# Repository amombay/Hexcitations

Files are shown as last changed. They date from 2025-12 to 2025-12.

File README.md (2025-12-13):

# Hexcitations
ENGN1735: Vibrations of Mechanical Systems Design Project, Active Particles
<div align="center">
  
</div>

Hexcitations is a design project for Brown University's School of Engineering course, ENGN1735: Vibrations of Mechanical Systems, completed by Andrew Mombay, Kaya Bruno, Helen Primis, and Sarah Nguyen in collaboration with the Harris Lab inclusive of Jack-William Barotta and Daniel Harris.

## Organization of this Repository
This repository contains the following folders:
- CAD Designs: This serves as the general purpose folder containing all CAD designs completed throughout the project, represented across the different iterations and phases of the project.
  - Cage Design: This sub-folder contains all designs of our cages, beginning with our circular cage model before moving to the rectangular, back-held cage model.
    - Iteration I: This sub-folder contains all designs of our intial, circular filament with PVC tubing linkages. These designs were later scrapped and replaced in favor of smaller, more compact linkages as significant issues were faced with friction and mass-dragging due to the sheer weight of the cage and the inability of the hexbug to provide adequate locomotion and movement of the cage for image tracking purposes.
    - Iteration II: This sub-folder contains all designs of our next model where we shifted towards building cages contained on the hexbugs back with a T-shaped marker for tracking purposes along with circular extrusions for the silicone linkages to attach to. This design was later modified and is thus currently redundnant to allow for a better fit on top of the hexbug and silicone linkage.
    - Iteration III: This represents the pre-cursor to our final linkage iteration. Modifications were made to the cage to encourage a better fit of both the cage and silicone linkage.
    - Iteration IV (Final): This represents our most current linkage with spacing for the QR codes for tracking and ensures best-fit for the hexbugs.
  - Linkage Design: This sub-folder contains all linkage mold designs including the 3.5, 4.5, and 5.5mm linkage molds.
    - Iteration I: This sub-folder contains all initial linkage mold designs
    - Iteration II (Final): This sub-folder contains all final linkage mold designs, including the 'key' mold design applied in our final experiemental model.
    - Iteration III (In progress): This sub-folder contains experimental mold designs that should not be used until further work is completed to prevent silicone leakage out of the mold. These molds are currently being explored to reduce extra silicone pieces around the mold and to enhance curing conditons.
  - Misc: This sub-filder contains all additional designs related to constraining the hexbugs movement such as a pole mount, jellyfish-modeled head, and final hexbug stations.
 - MATLAB: This serves as the general purpose folder containing all code regarding finding the material properties and constants along with all code needed to mock simulations of behaviors.
   - Iteration I: This sub-folder contained all previous versions of source code, inclusive of estimating material parameters, generating movies of simualtions, simulating behavior, and our initial tracking software. This code is currently redundant and encapsulated in our second iteration of code.
   - Iteration II (final): This sub-folder contains all finalized versions of iteration I, focusing on mocking the actual experiment through simulations and estimating the material properties and constants of the silicone linkages. All code referenced within these two categories is stored in this folder.
 - Tracking: This folder contains python files to track the hexbug filament. This is our final tracking software, utilizing the QR code method to process our videos.
- Written Remarks: This folder contains all written statements produced by the group, inclusive of our presentations, written materials produced (literature reviews, final written report, and more), our bill of materials, sustainability poster, and materials flow sheet.

## Background, Goals, & Modeling Approach
Background: Our project aims to study active particles and observe the collective behaviors and aggregated movement emergent upon coupling through a hexbug-based computational and physical model. In-depth research in this field occurred due to the development of high definition photography which allowed for the detailed scaling of the limb movements for invertebrates and vertebrates. The locomotive functions of the animal's appendages were linked to a central pattern generator in each organism, demonstrating that active particle are driven by autonomous collective movements without the direct influence of a central force. We look to create an accurate model for an adjustable linked filament to mimic cilia-like behaviors by utilizing Hexbugs and 3D-printed Hexbug-like particles to serve as a macroscopic version of the often microscopic particles referenced in the relevant literature. 

Key Goals
- Create an accurate model for an adjustable linked filament to mimic cilia-like behaviors by utilizing Hexbugs, exploring the interplay between the filament elasticity and activity
- Observe and analyze the collective synchronization behavior emergent upon coupling Hexbug active particles with variable bendability
- Investigate four-legged gaits, representative of quadriflagellates by attaching multiple Hexbug filaments to a center pin

Along with each phase of the project, we aim to implement the following modeling approach:
- Physical Modeling: To create the filaments, we plan on using linkages cast from a silicone mold to join the Hexbugs. This allows for semi-constrained movement along the x and y axes. A 3D-printed cage placed on top of each Hexbug allows the linkage to be affixed via prongs, as well as a show a QR code tracking marker to be utilized in Python image processing.
- Mathematical Modeling: Varying lengths of all of the silicone linkages cause the filaments as a whole to have different propensities to bend. To calculate the bendability of the filaments (elastoactive parameter), we first calculate the spring constants to verify the Young’s Modulus. We do this using image processing in MATLAB and can then calculate the corresponding torsional stiffness values and elastoactive parameter. 
- Data Collection: For each phase of this experiment, we use Python ArUco tracking to track the relative position and angular displacement of each Hexbug when fixed at a center point. Using these two elements, we can calculate the mean curvature and polarization for varying configurations of the apparatus upon changing the shape and length of the connection beam, the length of the filament, and the number of hexbugs on each filament.

## Findings & Future Directions
As of now, we have found the following:
- Hexbug filaments serve as an effective means of modeling and experimentally evaluating elasto-active systems in active matter, dynamic systems. Through our variation of both the linkage and filament length, we were able to establish that the onset of oscillation is both a function of the number of Hexbugs in the filament, N, and the σ, the elasto-activity of the linkage, as predicted by our mathematical model. Filaments with smaller values of σ showed straight-line trajectories with the onset of oscillation taking place somewhere between σ = 1.0071 and 1.8800, with higher values of σ producing longer periods of oscillatory behavior. Comparison between the experimental trajectories and the mathematical model showed relative agreement in the oscillation, mode shape, and phase behavior. Whilst quantitative differences remained between both the model and the experimental observations, likely due to friction and active force contributions, the model successfully captured the physics governing filament behaviors.
- Synchronization is possible with elasto-active elements through the application of silicone linkages between Hexbugs. Beyond our findings with single-filament behavior, we saw that Hexbug systems can show both synchronization and phase-locking behaviors. With the two and four-filament systems, we observed both synchronous behaviors in and out-of-phase in addition to desynchronization events likely due to asymmetric linkages, small differences in cage placement, and variations in Hexbug natural frequency. As such, this indicates that our model may allow for close comparison with biological cilia and flagella systems, mimicking complex biological behaviors. In addition, the ability to induce swimming-like modes and rotational motion highlights the ability of our model to study gait and locomotion in active matter systems.

Currently, our model is complete and ready to explore further scientific modeling and synchronization phenomenon. That being said, additional functionality is entirely possible and is highly recommended to reduce error and enhance both the scope and applications of our model. This includes:
- Building individual hexbugs to reduce any ‘drift’ error where the hexbugs have a general tendency to lean towards the right. Such drift is randomized, with some bugs seeing more significant drift than others due to manufacturing differences. As such, building our own hexbugs would eliminate this drift.
- To control for power differences, we could link our individually built hexbugs to a central power supply and eliminate any differences in supplied power to each component.
- To reduce issues in the silicone linkages, further work could be done on the encapsulated molds to prevent leakage and ensure the mold is completely full to reduce the error of excess silicone attached to the link. In addition, controlling the curing conditions with time, humidity, and temperature would enhance the accuracy of our results by unifying the material properties across all links.

Additionally, we pose the following questions as we continue our work:
- Coding/ Simulation Perspective
    - How can we more robustly track the orientation and positioning of our hexbugs beyond QR code tracking? Is there a way to further minimize any sort of “skipping” when some bugs are enduring lots of rotation in a short amount of time?
    - How can we reduce and/or better account for noise in our modeling?
    - Is there a way for us to test the active force of our particular Hexbugs (commercially or in-house) and would this help our simulation mirror what we are seeing in real-life? 
- Hardware and Design Perspective
  - How can we create a DV-powered homemade model to better simulate collective behavior and brownian motion as opposed to our current model?
  - How can we best implement our design to reduce Hexbug drift and skew towards one direction?
  - How can we best optimize and control cure conditions for the silicone linkages and how might other elastomer linkages impact our model? How do linkage length, stiffness, and cage geometry impact the range and modes of motion in our filament system?
  - How can we elicit multi-filament synchronization in Hexbug behavior? Is this theoretically plausible/ possible? To what extent can we see phase-locking and symmetrical movement compared to biological cilia?

 Given all of our remaining questions and findings, we propose the following next steps:
- Revise our physical model
  - By developing our own DV-powered hexbug design, we’d get to see its motion unimpacted by commercial manufacturing and thus get to validate our model without taking into account defects in supplier processing. In addition, this would allow us to control the native skew present in commercially available hexbugs by modifying our own design to reduce any drift effects. In addition, by further controlling the silicone mold curing conditions, we’d be able to enhance the accuracy of our model and ensure reproducibility.
- Improve our tracking software
  - Currently, our tracking software can only handle calculating the mean polarization and the mean curvature of a one-filament system. Expanding on our project, ideally, we would want to be able to accurately track a multifilament system, correctly identifying and tracking what Hexbugs correlate to what filament and comparing their relative angular motion, mean polarization, and mean curvature.
- Explore synchrony conditions
  - Through improving both the tracking and physical model, we would be able to begin enhancing our investigation into synchronization of our multi-filament model of which our findings would prove to be extremely beneficial to the scientific community in exploring how to model active particles to simulate real-world phenomenon.

## Building and Operating Instructions
  In order to build our device, the following steps should be taken:
- Hexbugs:
  - No direct modifications were made to the hexbugs themselves, however, prior to final modeling one should replace all batteries (LR44 coin batteries) in the hexbugs to ensure that power supplied is constant across all bugs.
- 3D Printed Hexbug Cages:
  - All hexbug cages were 3D printed using PLA filament and a BambuLabs A1 printed with an infill of 15%. Following printing, all supports were carefully removed and cages were visually inspected to ensure no damage had occurred.
- Silicone Linkages:
  - Molds were first 3D printed using PLA filament and a BambuLabs A1 printer with an infill of 15%. Four different molds were constructed of various lengths to measure the differences beam length had on bending motion of the filament. Following printing, all molds were visually inspected and supports were carefully removed to reduce the risk of breaking the mold. Our first renditions of the silicone molds were non-encapsulated whereas our final molds employed used a 2-piece, encapsulated system with pins used to ensure proper fit and mold orientation when casting.
  - To create the silicone mixture, we used a 2-part mixture and utilized a scale to carefully measure out 20 grams part A and 20 grams part B of the mixture to ensure equal aliquots were used. This was then thoroughly mixed using a wooden popsicle stick and then poured carefully into the molds. Molds were purposefully overfilled to ensure all parts of the mold were uniformly filled. Molds were then cured in open-air conditions at 70F and humidities of 20-50% for at least 24 hours.
  - Following a cure time of at least 24 hours, the linkages were then carefully pulled from their molds, visually inspected for any deformities, and excess silicone was trimmed off.
- Central Body/ Hexbug ‘Station’:
  - All versions of the hexbug station, circular, rectangular, and individual were 3D printed using PLA filament and a BambuLabs A1 printer with an infill of 15%. Following printing, all supports were carefully removed and the station was visually inspected to ensure no damage had occurred.
- Hexbug Station and Hexbug Cage Silicone Clips:
  - Both versions of the Hexbug silicone clips for the station and cages were 3D printed using PLA filament and a BambuLabs A1 printer with an infill of 15%. Following printing, all supports were carefully removed and the clips were visually inspected to ensure no damage had occurred.
- QR Codes:
  - All QR codes were printed on standard 8x11 A4 paper and carefully cut out to ensure the QR code had a white border to ensure accurate tracking due to the color of the Hexbug cage filament (black). 

Upon finishing all individual components, the cages were placed on top of the Hexbug and adjusted until the fit was snug and the Hexbug was pushed as far forward as possible against the cage’s front ‘fence’ to ensure uniform fit across all hexbugs. The linkages were then placed into the pin and the PLA silicone clips were clamped down onto the linkage until snug. The frontmost cage was then connected to the station and the station silicone clip was used to secure the Hexbug filament to the station. Finally, double sided tape was used to secure the QR codes onto the back of each bug for tracking purposes.

In order to operate our device, the following steps should be taken:
- After the finalized assembly is complete, as described above, the full assembly was placed on a white backing sheet for contrast and a tripod was set up to record the filament’s oscillations.
- Each bug was then individually turned on and the filament was then recorded. After recording was complete, videos were saved and all post-processing of the video was then conducted in Python and compared to the simulation predictions done in MATLAB.

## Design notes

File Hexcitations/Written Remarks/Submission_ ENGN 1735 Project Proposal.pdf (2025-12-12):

ENGN1735 Active Particles Project Proposal Sarah Nguyen, Helen Primis, Andrew Mombay, & Kaya Bruno Mentor: Jack-William Barotta
Due October 14, 2025
Project Name: HexCitations

Contents:

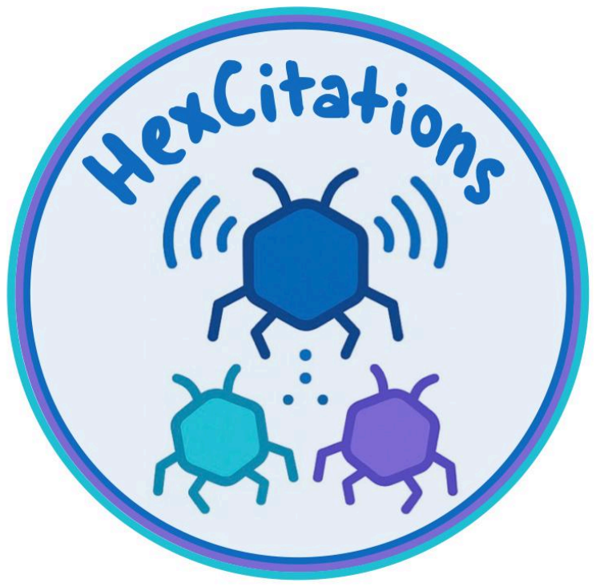
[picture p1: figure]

### 1. Background and Brief Literature Review 2. Key Questions 3. Experimental Workflow and Schematics

a. Phase I
b. Phase II
c. Phase III

### 4. Data Collection and Aim of Iteration

a. Phase I
b. Phase II
c. Phase III

### 5. Modeling, Numerical Techniques, and Materials 6. Semester Timeline and Group Member Roles 7. Project Deliverables and Transfer of Knowledge 8. Appendix

a. Bibliography

### 1. Background and Brief Literature Review

The background of our project lies with the study of active particles and observations of the collective behaviors emergent upon coupling. Unlike true Brownian motion, linked active particles harness their own energy and have the capability for complex collective behaviors to arise.

1 There is
evidence of collective behaviors with active particles resulting in self-propelling locomotive functions, resource collection, local environmental restructuring, and particle aggregation.

2 The foundations of this
study are cited as being rooted back to the philosophical fundamentals of Aristotle: the whole is greater than the sum of parts.

3 Considering the example of biotechnically-based robotics systems, the behavior of active particles is driven by autonomous collective movements without the direct influence of some sort of central force; the critical nature of this study is how the “random” particles, when linked together, result in an aggregated movement.
The onset of research in this field occurred due to the development of high definition photography which allowed for the detailed scaling of the limb movements for invertebrates and vertebrates. The locomotive functions of the animal's appendages were linked to a central pattern generator in each organism that did not send feedback to the neural system thereby enacting the movement. This is connected to our investigation of aggregated movement mentioned in the previous paragraph.

4 Different
locomotive actions can be linked to a certain number of filaments stemming from a fixated central body. Two appendages could represent swimming, four could represent trotting, eight could represent rotary breast stroke of flagella, and sixteen could mimic the wave motion of a series of cilia.

5 The study of
collective behaviors usually falls under the Viscek model which focuses on the emergence of scaled dynamics from independent particles. The model exists with much freedom, saying “The only rule of the model is that at each time step a given particle driven with a constant absolute velocity assumes the average direction of motion of the particles in its neighborhood with some random perturbation added.”

6
Sources cite the alignment of velocities as a result of both self-propelled forces and “social forces,” when applicable.

7
Taking the somewhat disconnected but overarching plethora of research in the realm of active particle behavior, our project aims to employ Hexbugs and 3D-printed Hexbug-like particles to serve as a macroscopic version of the often microscopic particles referenced in the relevant literature.

8
Understanding and taking into account that the inertia of our active particles can affect the linked movements of our systems, we will aim to create an accurate model for an adjustable linked filament to mimic cilia-like behaviors. The first rendition of this filament will be battery based, with a second stage evolution resulting in a direct voltage sourced filament which is independent of batteries in the active particles. Time permitting, we will apply our filament model to model the appendage based movement of a jellyfish and explore how different orientations and combinations of filament power and length affect the velocity of our model’s movement.

9 Our key questions and project workflow are outlined below in this project proposal.

9 Miles, Jason G, et al., 3.

8 3D Printable Hexbug Design and Instructions, Blog Link. (https://stldenise3d.com/vibrobugs-3d-printed-brush-bots/)

7
Ibid, 4.

6 Baconnier, et al, 3.

5
Ibid, 3.

4 Wan, 2.

3 Levay, et al., 2.

2 Sinaasappel, et al., 1.

1 Barona Balda, et al., 847.

### 2. Key Questions

A. How can we build a cilia-like filament by employing 3D-printable hexbugs and mechatronic principles?
B. How do different orientations of hexbug coupling influence their collective actuation?
C. How does spring stiffness influence synchronization and sustained oscillations in elastic networks?
D. Can we achieve biomimicry with our model?

### 3. Experimental Workflow and Schematics

a. Phase I:
For the first experimental phase of this project, we will utilize Hexbug Nanos from the Harris lab as the macroscopic active particles within the filament. We will design shells to contain each particle and provide a linkage point between each discrete bug. The filament will be attached to one fixed non-powered source, such as a cilia attached to the parent body.
b. Phase II

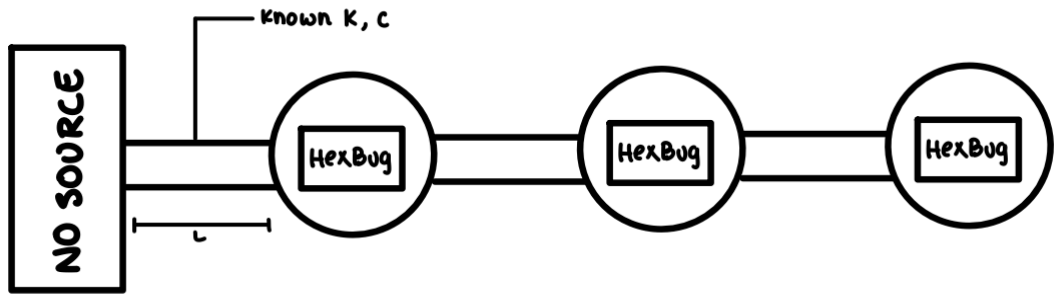
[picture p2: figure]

For the second phase, we will 3D print and construct Hexbugs that can be connected via wiring to a fixed direct voltage source, eliminating the need of the battery powered Hexbug Nanos. This design will be modular to allow for adjustable filament length and attachments.

c. Phase III

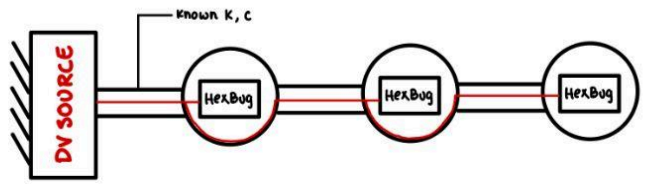
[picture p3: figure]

Time permitting, we will engage with the concept of biomimicry using the DV-source based filament design by having multiple appendages attached to one unfixed central body, mimicking a jellyfish. The goal of this phase is to investigate the Hexbug orientations that move the fastest, considering different lengths and numbers of cilia attached to the beam.

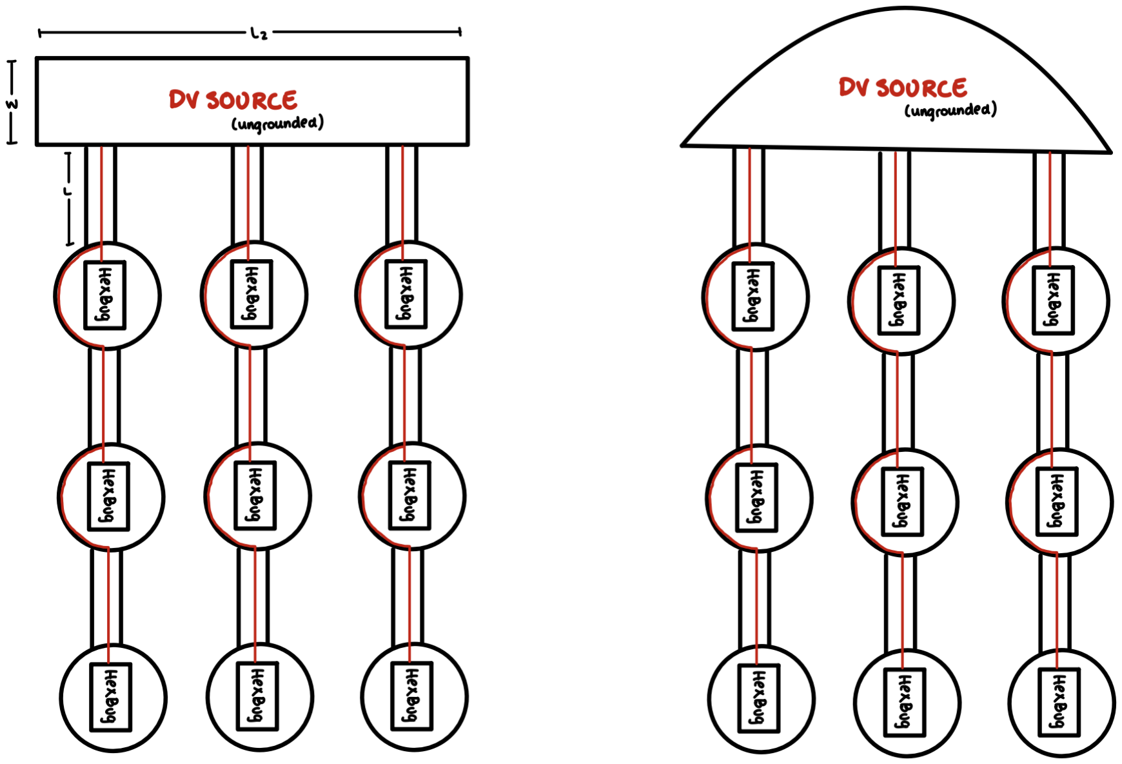
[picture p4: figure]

### 4. Data Collection and Purpose of Iteration

a. Phase I: For the first iteration of our filament, we will use MATLAB image tracking to track the relative displacements and velocities of each particle to the fixed base. The purpose of this iteration is to understand the aggregate movement of the linked active particles when using battery-based Hexbugs and get a strong foundational prototype for future facets.
b. Phase II: For the second phase, we will perform the same data collection set as Phase 1, now employing a DV source based model instead of the battery Hexbugs to see if results are replicable. The nuance of modular design for this phase will allow us to easily change the number of particles attached to the fixed base to discover different aggregated movements which are dependent on adjustable features.
c. Phase III: From the third phase, we will collect average velocity data for varying configurations of the apparatus upon changing shape and length of connection beam, length of filament, number of hexbugs on each filament. The purpose of this iteration is to apply the principles developed in the previous phases to replicate a biological phenomenon.

### 5. Modeling, Numerical Techniques, and Materials

To complete this project, we anticipate primarily scaffolding existing resources on Hexbug construction to build our framework filament.

10 This will be primarily accomplished through utilizing 3D-printing methods and applying CAD skills to construct each individual Hexbug. Considering the driving electronics for this project, we will utilize pager motors and a central power supply to supply power to all hexbugs concurrently. We plan on using flexible PVC tubing to join form Hexbug filaments to allow for semi-constrained movement along the x and y axes. A summary of our projected components and costs can be found below.
When analyzing the movement of our hexbugs, we may want to collect additional points of data beyond velocity and position that would allow us to better understand the phenomenon. We can break down their behavior based on their position, velocity, angle of movement, and general error due to inconsistencies in the hexbugs and the surface. As our experiments will generate a large amount of data, we will use MATLAB image processing to streamline the data collection process. This allows us to consistently measure the tracked values of the Hexbug’s movement.
Item | # Units | Cost | Purpose
PLA Filament (Black) | 1 spool | N/A (Personal filament will be used) | Used to build individual components (Hexbug body, filaments, etc.).
Pager Motors | 20 (1 pack) | $14.29 (Amazon) (https://www.amazon.com/Xnrtop-20Pcs-3500RPM-Pager-Vibration/dp/B09TZZT8YC?sp_csd=d2lkZ2V0TmFtZT1zcF9hdGY) | Generate the vibrations needed to generate movement for each Hexbug.
Wiring, 20 AWG | N/A | N/A (Personal wiring will be used) | Links each individual bug up to a central power supply.
PVC Tubing | 10ft | $8.99 (Amazon) (https://www.amazon.com/Metaland-Silicone-Tubing-Brewing-Winemaking/dp/B08XM1V475?sp_csd=d2lkZ2V0TmFtZT1zcF9hdGY) | Connects each bug cage to form a filament.
Ball Bearings (6705-2RS, 25*32*4 mm) | 20 (2 packs) | $29.58 (Amazon) (https://www.amazon.com/uxcell-6705-2RS-Groove-Bearing-Bearings/dp/B0CNX5FZY4) | Allows for unconstrained movement of each Hexbug cage and reduces risk of wire torsion.
Power Supply | 1 | N/A (SOE/ BDW central power supplies will be used) | Allows us to regulate voltage/ amperage to determine how voltage changes change filament behavior.
Microswitches | 150 (1 | $6.99 (Amazon) (https://www.amazon.com/gp/product/B09R3Y6MMN?linkId=6482647e5f9c6a39063e86963b218b85&language=en_US) | Allows us to turn on and off each filament.

10 3D Printable Hexbug Design and Instructions, Blog Link. (https://stldenise3d.com/vibrobugs-3d-printed-brush-bots/)

| pack)
Total Estimated Cost | $59.85
Total Budget Remaining | 140.15 | Excess budget reserved for the potential purchase of Hexbug Nanos, supplemental wiring, other materials for filament connections, and other adaptations needed throughout the design process

### 6. Semester Timeline and Group Member Roles

Regarding our timeline, we anticipate using our remaining time (9 weeks) in the following manner, with roles and general task priorities outlined below.
- 10/17: Finalize the scope of our project, order initial materials, finalize CAD modeling for the individual Hexbug cage.
- 10/24: Build individual Hexbugs for each filament, assemble initial filament and modify CAD (if necessary) to fit tolerances, scaffold central power supply, code tracking software.
- 10/31: Begin initial testing, revising linkage materials if required, test tracking software to analyze filament behaviors, work on progress presentation slide deck
- 11/6: Progress presentations in lecture and slide deck, and group midterm evaluation
- 11/7: Revise tracking software & bugs and begin experimental trials
- 11/14: Continue experimental trials, finalize parts list, determine if any additional components are needed, revise testing criteria if need be
- 11/21: Analyze experimental data
- 11/28: Finish data analysis and begin work on final deliverables
- 12/5: Continue work on final deliverables & presentation framework
- 12/12: Finalize final deliverables, practice presentations, and wrap up any loose ends.
- 12/13: Final presentation of deliverable, and final group evaluations
Regarding individual roles, Andrew will be responsible for the CAD, hardware, and mechatronics components of the project, taking priority over mechanical linkage design. Sarah will be responsible for developing the filament linkages and leading data processing including the development of our tracking software. Kaya will be responsible for hardware, schematics, and data reporting through taking priority on the experimental design, revisions, and generalized testing. Helen will be responsible for data processing and experimentation, combining skills to assist in the development of our tracking software and adapting it as we progress in our study.

### 7. Project Deliverables and Transfer of Knowledge

From our findings, we hope to advance the work of the active matter community, contributing to the simulation of natural phenomena through the application of small robotics, particularly for ongoing projects in the Harris and Wilhelmus labs. Through our experimentation, we hope to gain a better understanding of jellyfish locomotion and thus contribute to the marine ecosystem community. To advance such work, we intend on writing up a report summarizing our findings, including demonstrations of our Hexbug prototype. We will also create an open source GitHub page including our CAD designs, code, raw and processed data, and a general framework to ensure experimental reproducibility.

### 8. Appendix

a. Bibliography
Baconnier, Paul, Olivier Dauchot, Vincent Demery, et al. “Self Aligning Polar Active Matter.” Reviews of Modern Physics 97, no. No. 1 (2025): 1–26.

Barona Balda, Angelo, Aykut Argun, Agnese Callegari, and Giovanni Volpe. “Playing with Active Matter.” The American Journal of Physics 92 (November 2024): 847–58.

Levay, Sara, Axel Katona, Hartmut Lowen, Raul Cruz Hidalgo, and Iker Zuriguel. “Cluster Dynamics in Macroscopic Photoactive Particles.” Physical Review Letters 135, no. 098301 (2025): 1–7.

Miles, Jason G., and Nicholas A. Battista. “Naut Your Everyday Jellyfish Model: Exploring How Tentacles and Oral Arms Impact Locomotion.” Fluids Journal 169, no. 4 (2019): 1–43.

Sinaasappel, R., K.R. Prathyusha, Harry Tuazon, et al. Collecting Particles in Confined Spaces by Active Filamentous Matter. May 9, 2025, 1–27.

Wan KY. 2019 Synchrony and symmetry-breaking in active flagellar coordination. Phil. Trans. R. Soc. B 375: 20190393.

3D Printable Hexbug Design and Instructions, Blog Link. (https://stldenise3d.com/vibrobugs-3d-printed-brush-bots/)

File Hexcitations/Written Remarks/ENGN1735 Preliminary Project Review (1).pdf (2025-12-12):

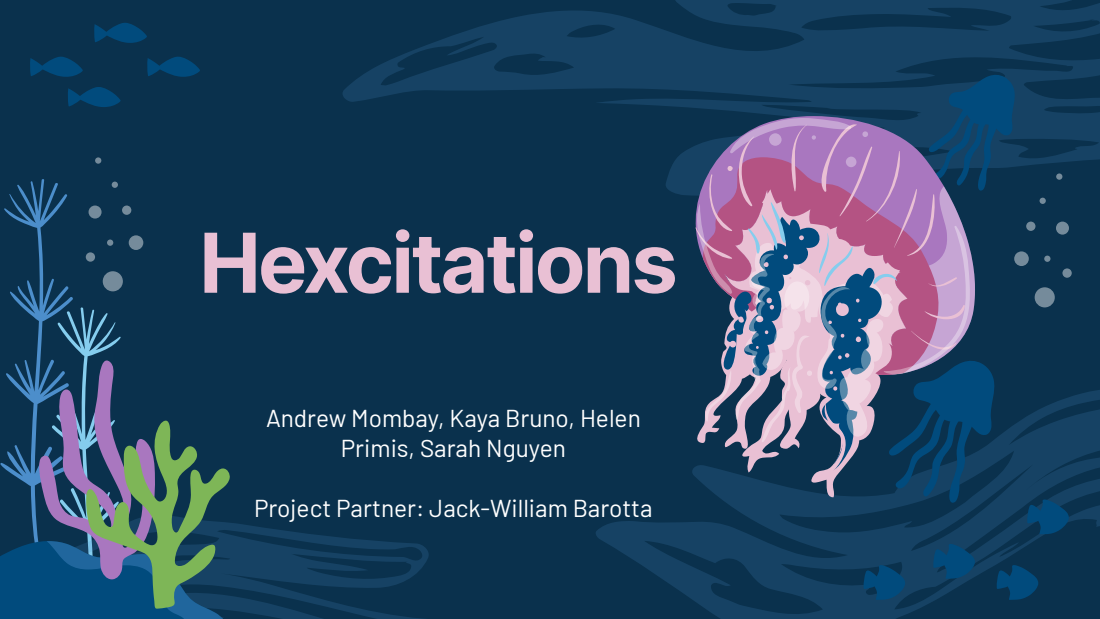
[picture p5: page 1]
Hexcitations

Andrew Mombay, Kaya Bruno, Helen
Primis, Sarah Nguyen

Project Partner: Jack-William Barotta

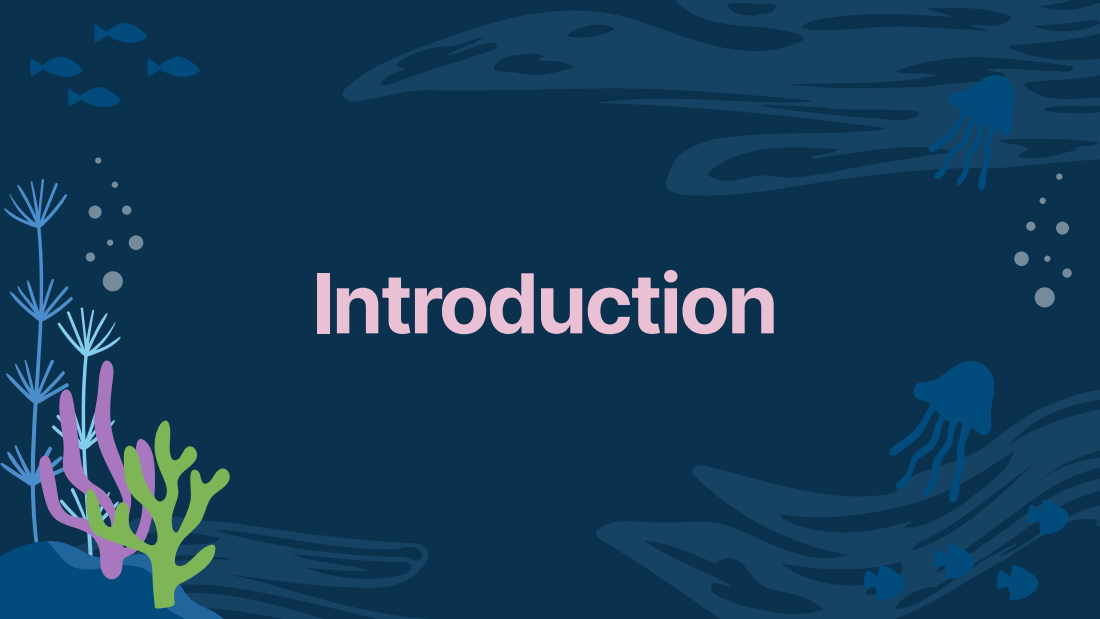
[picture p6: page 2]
Introduction

# Active Particle & Collective Motion

What makes a particle active? An
active particle is one that takes energy from its environment in order to move autonomously. When active particles interact with one another, they have the ability to exhibit collective motion. Collective motion behaviors are seen across nature, including
colonies of bacteria, schools of
fish, and swarms of birds.

An application of collection motion includes investigation into the mechanics of animal appendages. One study models locomotive patterns of animals by analyzing microalgae, demonstrating that the locomotive functions of the animal's appendages are linked to a central pattern generator, and that active particle are driven by autonomous collective movements without the direct influence of a central force. In this way, animal appendages can be modeled as an active filament.

# HexBugs as Active Particles

Hexbugs can serve as macroscopic representations of the microscopic particles referenced in the relevant literature on active particles. Taking into account that the inertia of our active particles can affect the collective movement of the system, coupled ODEs can model the aggregate motion upon linking the discrete Hexbugs together. We can design different elastic linkages by varying length and thickness to discover different modes of motion. Past researches have coupled the hexbugs with combinations of springs, rubber, soft plastic, and different styles of cages to provide support for the connections. Cilia-like filaments and webbed particles provide a foundation for our exploration into the world of active particles

# Our Goals

Our project aims to study active particles and observe the collective behaviors emergent upon elastic coupling. We look to create an accurate model for an adjustable linked filament to mimic cilia-like behaviors by utilizing Hexbugs and 3D-printed Hexbug-like particles. We will create both a battery based and direct voltage sourced filament, observing it’s motion when one end is fixed in place.
For further biological application, we look to model the appendage-based movement of a jellyfish by attaching multiple active filaments to a central body. In particular, we model ctenophores, or comb jellies, which employ bands of cilia to swim. As such, the design of these active filaments allows for the controlled study via a tabletop robotic setup that exhibits behaviors/observation of both cilia behavior at the microscale and ctenophores behavior at the macroscale. Furthermore, the modular design of the linkages between Hexbug particles will allow us to explore how different orientations and combinations of filament power and length affect the interplay between the filament elasticity and activity.

# Key Questions

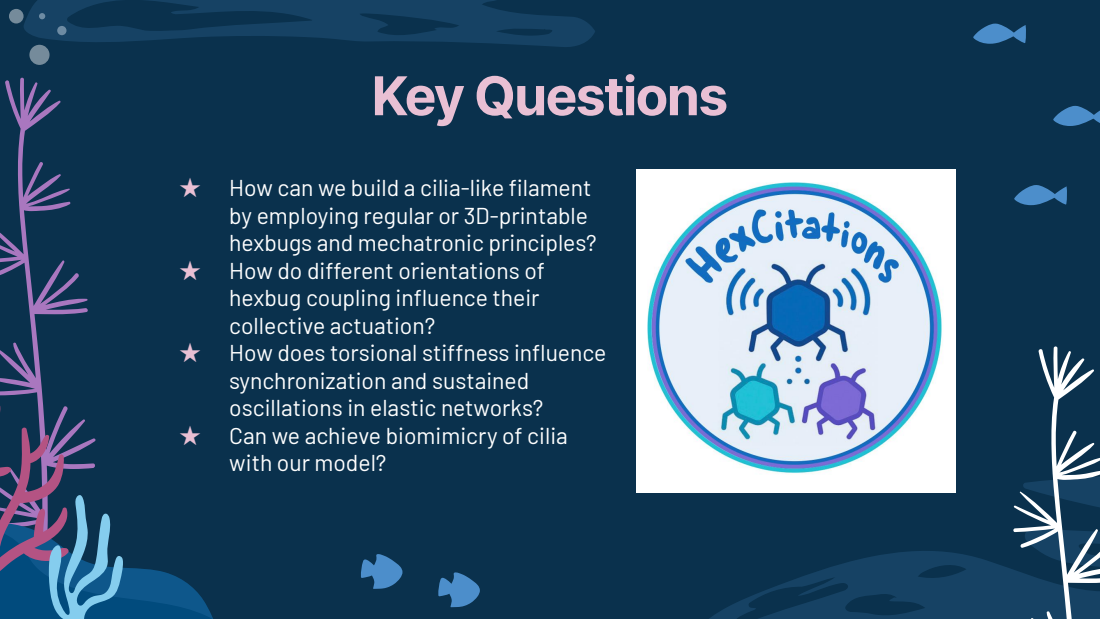
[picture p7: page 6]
How can we build a cilia-like filament; How do different orientations of; How does torsional stiffness influence; Can we achieve biomimicry of cilia

by employing regular or 3D-printable
hexbugs and mechatronic principles?
hexbug coupling influence their
collective actuation?
synchronization and sustained
oscillations in elastic networks?
with our model?

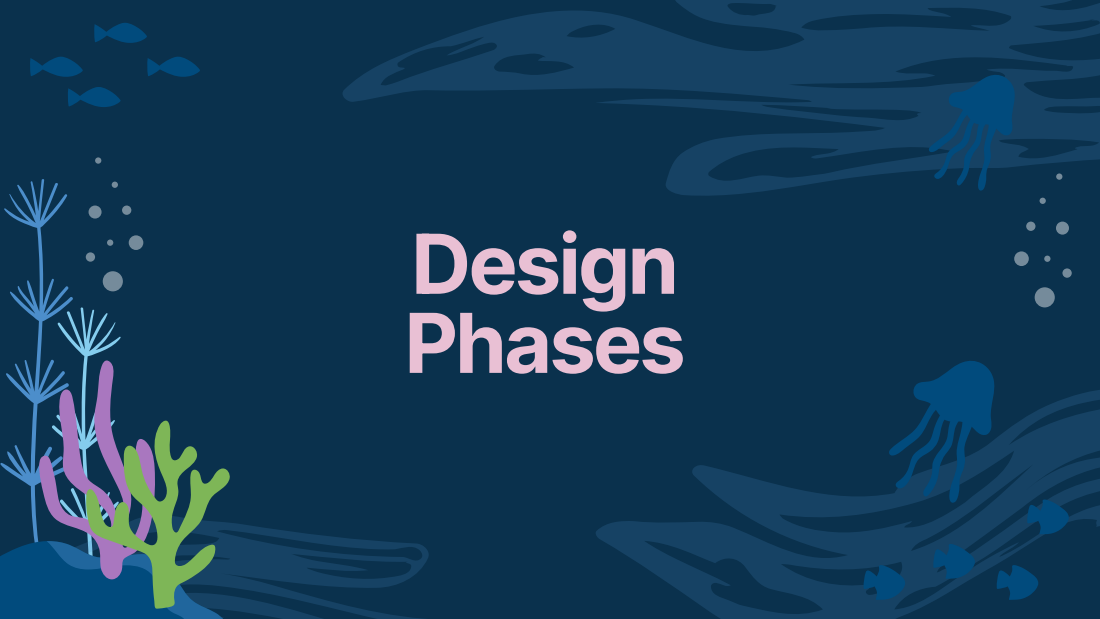
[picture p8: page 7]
Design Phases

# Experimental Approach

PHASE I: We utilize Hexbug Nanos from the Harris lab as the macroscopic active particles within the filament. We provide a linkage point made from a silicone mold between each discrete bug. The filament will be attached to one fixed non-powered source, such as a cilia attached to the parent body.

PHASE II: We 3D print and construct Hexbugs that can be connected via wiring to a fixed direct voltage source, eliminating the need of the battery powered Hexbug Nanos. This design will be modular to allow for adjustable filament length and attachments.

PHASE III: TIme permitting, we engage with the concept of biomimicry using the DV-source based filament design. We attach multiple appendages to one fixed central body, mimicking a jellyfish, investigating the Hexbug orientations that generate the most thrust considering different lengths and numbers of cilia attached to the beam.

# Approach Phase I

Experimental Workflow: Using the Hexbugs from the Harris Lab and silicone rubber linkages developed in self-designed molds, we will start by making a singular filament. This filament will be attached to a stationary body for us to explore the movements which arise.

Modeling: We use MATLAB image tracking to track the relative displacements and velocities of each particle to the fixed base. The purpose of this iteration is to understand the aggregate movement of the linked active particles when using battery-based Hexbugs and get a strong foundational prototype for future facets.

# Approach Phase II

Experimental Workflow: We 3D print and construct Hexbugs that can be connected via wiring to a fixed direct voltage source, utilizing pager motors. This design will be modular to allow for adjustable filament length and attachments.

Modeling: We will perform the same data collection set as Phase 1, now employing a DV source based model instead of the battery Hexbugs to see if results are replicable. The nuance of modular design for this phase will allow us to easily change the number of particles attached to the fixed base to discover different aggregated movements, dependent on adjustable features.

# Approach Phase III

Experimental Workflow: We engage with the concept of biomimicry using the DV-source based filament design. We attach multiple appendages to one fixed central body, mimicking a jellyfish, investigating the Hexbug orientations that move the fastest considering different lengths and numbers of cilia attached to the beam.

Modeling: We collect mean curvature and polarization data data using particle tracking on MATLAB for varying configurations of the apparatus upon changing shape and length of connection beam, length of filament, number of hexbugs on each filament. The purpose of this iteration is to apply the principles developed in the previous phases to replicate a biological phenomenon.

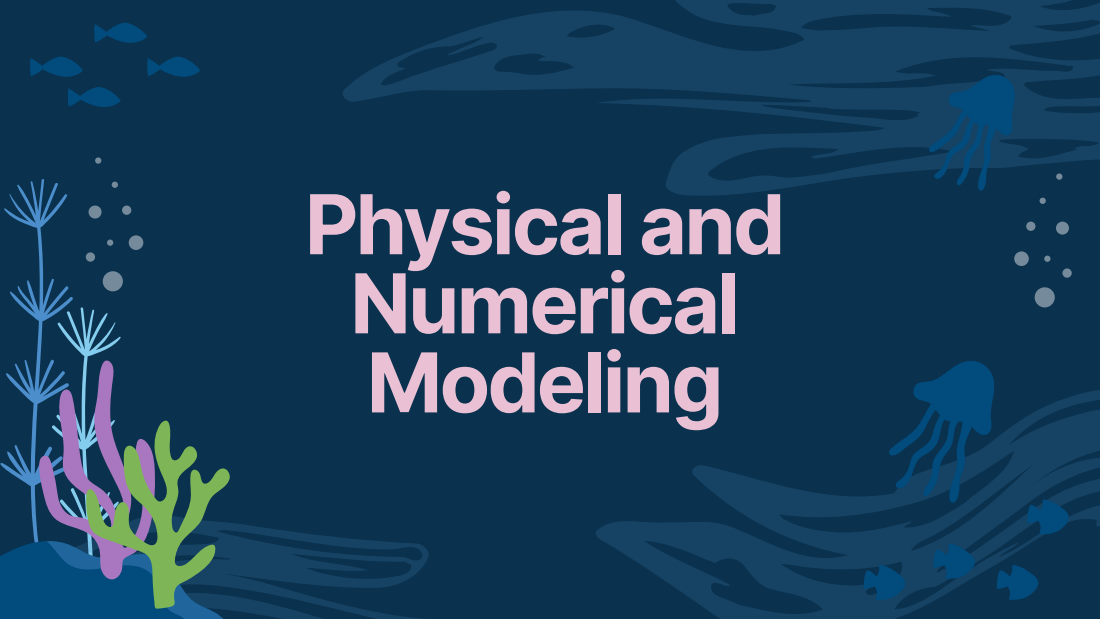
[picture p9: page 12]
Physical and Numerical Modeling

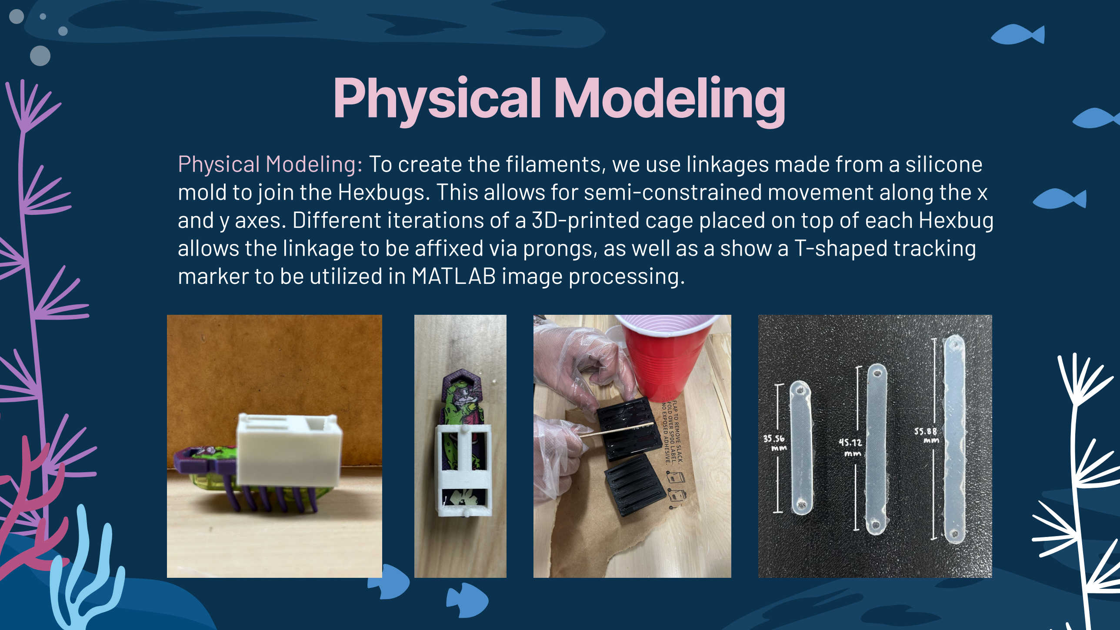
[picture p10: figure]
Physical Modeling

Physical Modeling: To create the filaments, we use linkages made from a silicone mold to join the Hexbugs. This allows for semi-constrained movement along the x and y axes. Different iterations of a 3D-printed cage placed on top of each Hexbug allows the linkage to be affixed via prongs, as well as a show a T-shaped tracking marker to be utilized in MATLAB image processing.

# Parameter Estimation

Spring Constant (k): To determine the spring constant, k, of each linkage length, we hung known masses (m) from the linkages and used MATLAB image processing to calculate displacement (x). The spring constant k is given by k = F/x where F=mg.

Young’s Modulus (G): Determining the spring constant, k, allows us to calculate the Young’s Modulus, G = kL/A where L = length of linkage, and A = cross sectional area of the linkage. The length of the small, medium, and large linkages were determined as 35.56 mm, 45.72 mm, and 55.88 mm respectively. We determined A = 11.91 mm^2.

Torsional Constant (C): After computing the Young’s Modulus for each linkage, we then defined the torsional constant C = GJ / L, where the second moment of area

Elastoactive Parameter (σ): From supplementary material we define the elastoactive parameter σ = FaL/C where Fa is average force of Hexbug while pinned given as 15.7 土 3.1 mN, The elastoactive parameter represents the ratio between active forces to bending forces. When sigma is small we expect straight line trajectory, and when sigma is large we have limit cycle trajectory for the Hexbugs.

# Parameter Estimation

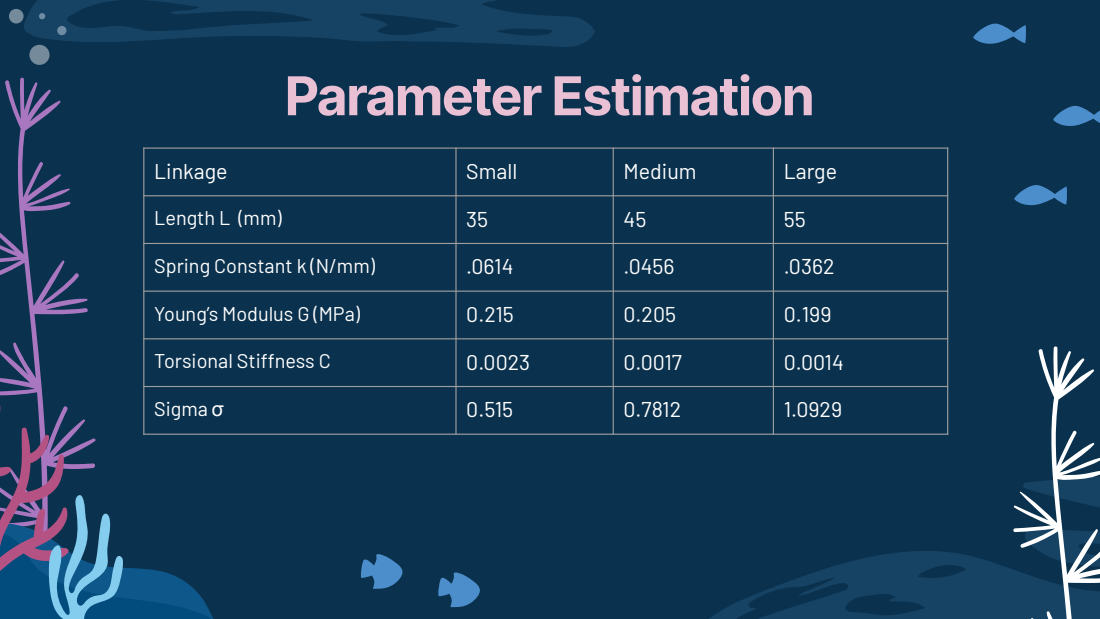
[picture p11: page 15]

Linkage | Small | Medium | Large

Length L (mm) | 35 | 45 | 55

Spring Constant k (N/mm) | .0614 | .0456 | .0362

Young’s Modulus G (MPa) | 0.215 | 0.205 | 0.199

Torsional Stiffness C | 0.0023 | 0.0017 | 0.0014
Sigma σ | 0.515 | 0.7812 | 1.0929

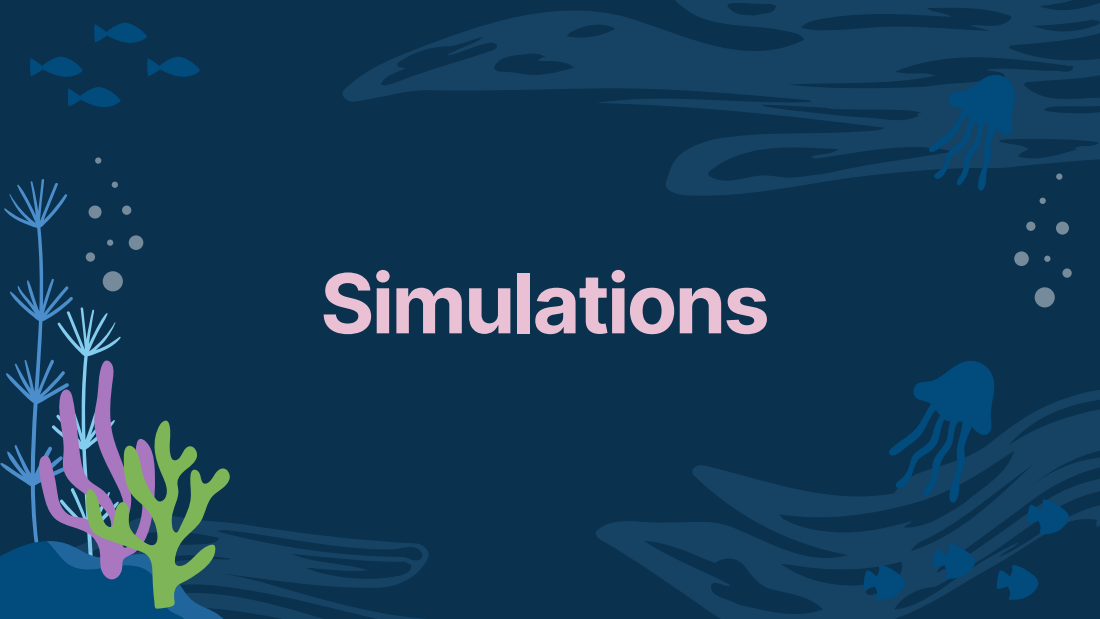
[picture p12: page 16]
Simulations

# Simulation Overview

Simulation: Employing equations from Ellen Zheng’s 2023 paper on aggregated movement amongst N number of particles. Using Matlab to show how a singular filament with Hexbugs connected facing inward toward the pivot will move in relation to each other.

Data Collection: For each phase of this experiment, we use MATLAB particle tracking to track the relative displacements and velocities of each particle (x, y, theta) to the fixed base. This allows us to consistently measure the tracked values of the Hexbug’s movement. We can break down their behavior based on their position, velocity, angle of movement, and general error due to inconsistencies in the hexbugs and the surface. In particular for phase III, we collect mean curvature (final angle - initial angle) and polarization data (orientation of the self-propelling particles) for varying configurations of the apparatus upon changing shape and length of connection beam, length of filament, number of hexbugs on each filament.

# Active Particle Movement

★ | Employing governing equations and supplemental material for the filament based
| experiments found in a 2023 paper authored by Ellen Zheng to simulate and illustrate
| the x-y movement and the orientation development of theta
★ | F_a is given by the nature of the hexbug, L is the length of the hexbug, C is something
| we need to compute today depending on silicone, tao is something never used by the
| authors (dimensionless time), gamma is in the paper
★ | In turn, we will see the change in potential energy equal to the change in work of the
| system
★ | Using the summations and dimensionless parameters, we can develop a series of n
| coupled ODEs to run through a solver and fine the orientation and trajectory of each
| particle

# Active Particle Movement

★ | Forces are in x, energy equation is in theta
| ○ Thus, the simulation script takes forcing equations and translates them all
| into theta to graph orientation
| ○ Then uses trigonometric relationships to graph XY trajectory back in those
| dimensions
| ○ If we have too much noise, the phenomena would not be visible
★ | Of Note: This simulation does not take noise
| ○ Demonstrates through experimental data that the more noise present in
| the trial, there is a decreasing nature of aggregated movement
| ○ If we were to account for noise, we no longer would be able to employ
| ODE45 in our Matlab simulation to solve our coupled equations
| ○ In turn, we could develop our own solver in Matlab or Python to account for
| the random nature of noise and see how it affects our preliminary
| simulation results

# Simulation Animation

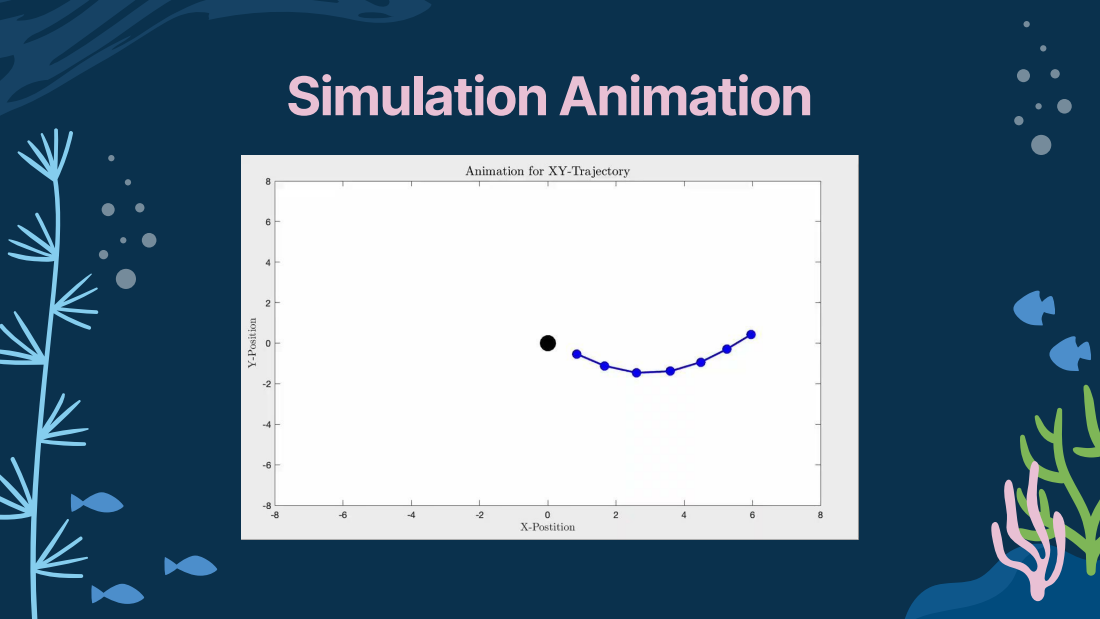
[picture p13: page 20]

# Simulation Plotting

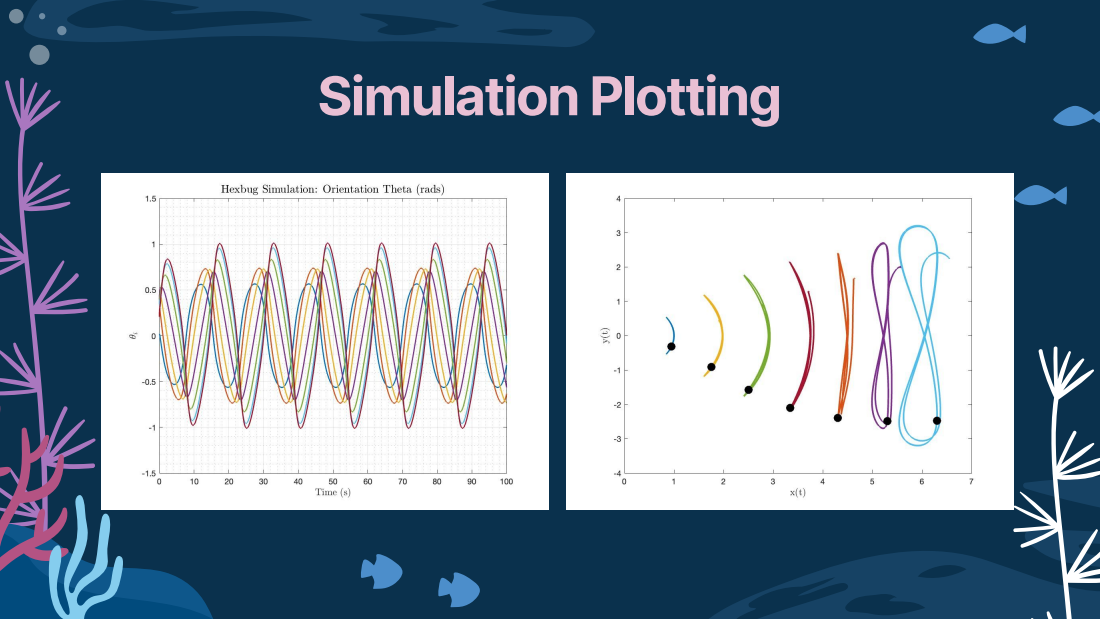
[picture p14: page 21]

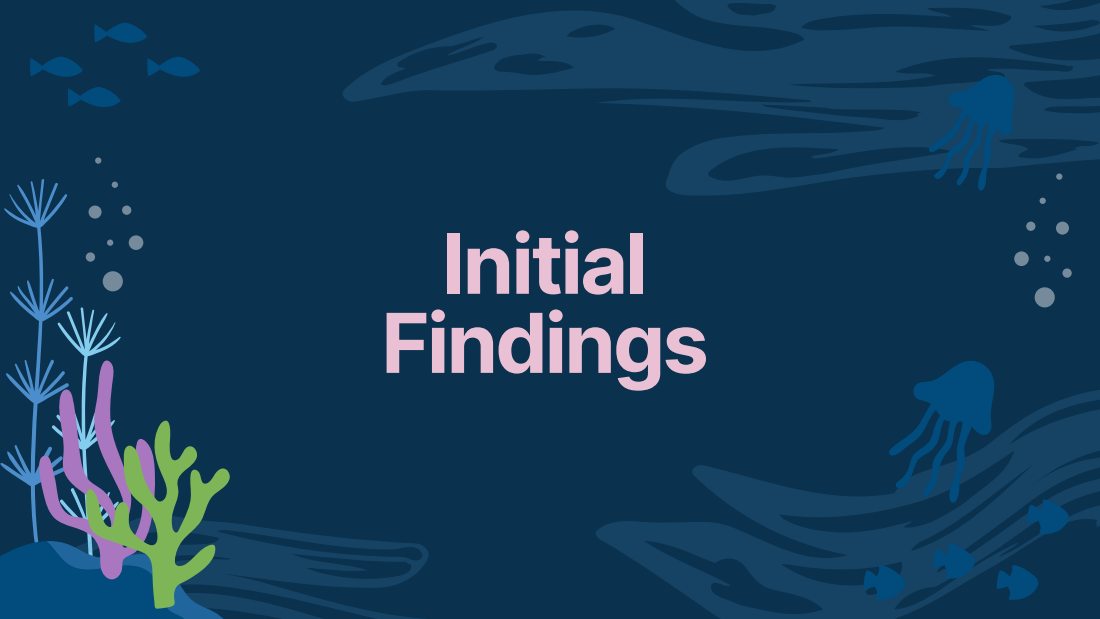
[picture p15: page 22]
Initial Findings

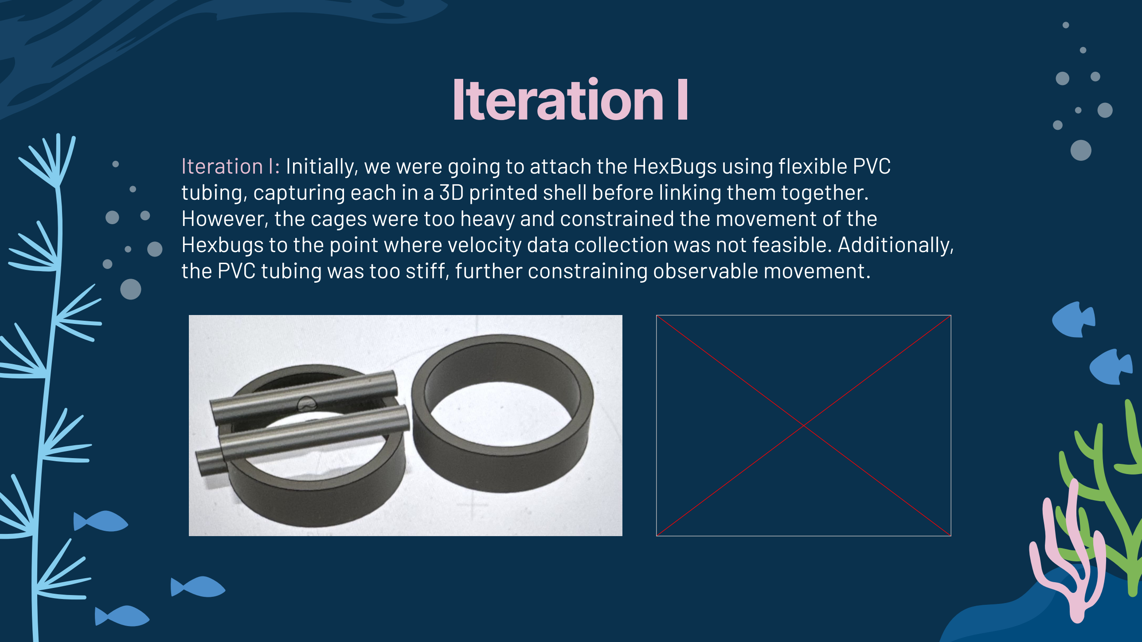
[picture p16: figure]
Iteration I

Iteration I: Initially, we were going to attach the HexBugs using flexible PVC tubing, capturing each in a 3D printed shell before linking them together. However, the cages were too heavy and constrained the movement of the Hexbugs to the point where velocity data collection was not feasible. Additionally, the PVC tubing was too stiff, further constraining observable movement.

# Iteration II

Iteration II: Considering the restricted movement of the Hexbugs due to the weight of the cages and stiffness of linkages, we looked to amend our setup by connecting the Hexbugs directly and using string as the linkage to increase mobility. From this, we were able to plot orientation vs time and X-Y trajectories.

Takeaways from Plots:
- Properly able to track trajectory
- Encountering sensitivity in the theta direction
- Issues with periodicity
Next moves:
- Add smoothing to the theta function in the code and account for periodic rotations of the bug
- Design cages with orientation-tracking design

Tracker Code
One Bug with No Cage

# Iteration II - One Bug Plotting

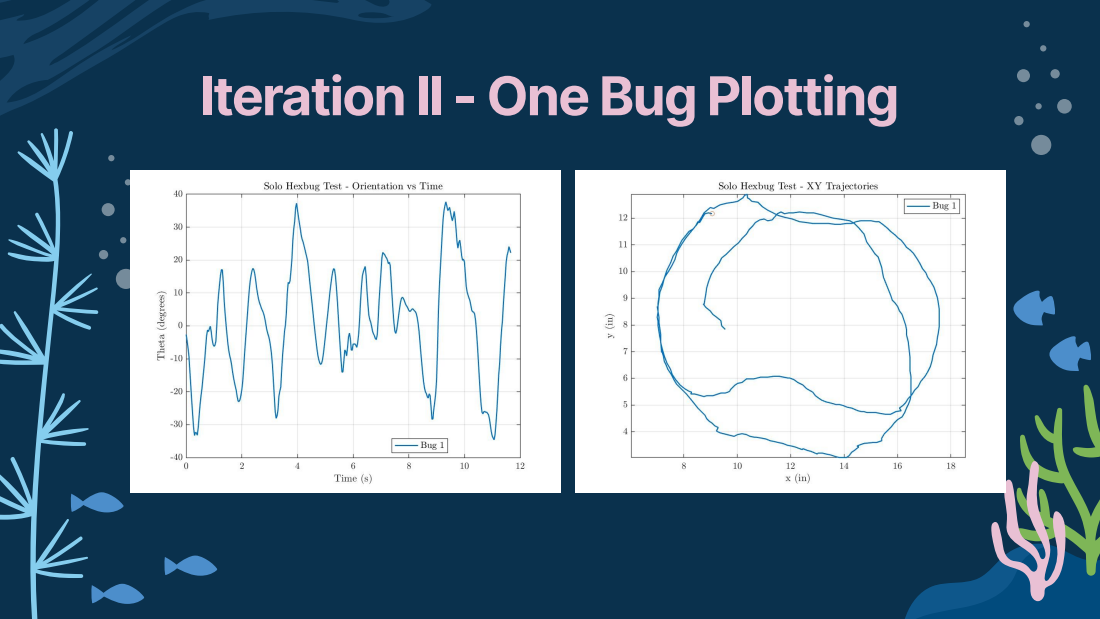
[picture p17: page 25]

Iteration III: Upon identifying issues with initial tracker code, we designed a lighter cage mounted on top of the Hexbug, with “T” on it to try and get Matlab to pick up the orientation better. The cage also enabled us to attach the string connections closer to the center of the bug and near where the bulk of the mass is.

Takeaways from Plots (Next Slide):
- Proof of concept that the XY tracking can account for multiple bugs in close proximity to each other
- Theta is still struggling with the periodic nature of the bug movement
Next Moves:
- Adapt theta tracker to not set a resetting zero line, which is why we were getting the recurring jumps in theta
- Make theta a summation of the orientation to see a linear relationship

Tracker Code
Two Bugs with Cages

# Iteration III

# Iteration III - Two Bugs Plotting

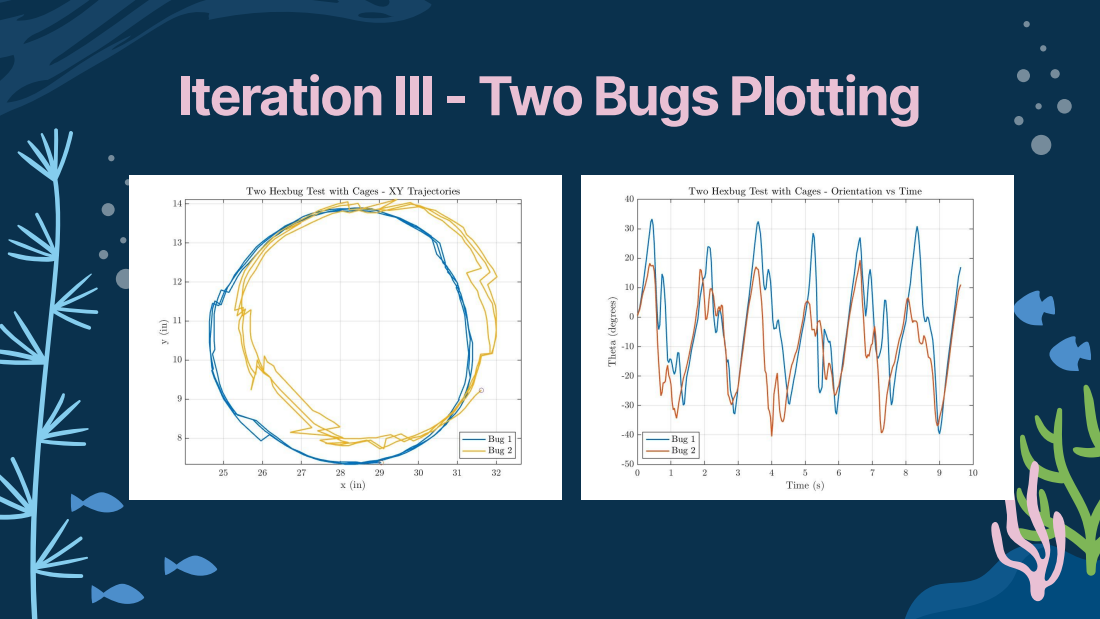
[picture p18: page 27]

Takeaways from Plots:
- Properly able to track trajectory and theta Next moves:
- Develop shorter/stiffer linkages in an attempt to mimic the jellyfish-like phenomenon
- So the linkages will not fold over when all running inward toward a pivot point
- Re-incorporate scaling through ruler

Tracker Code
Three Bugs with New Cages

# Iteration IV

Iteration IV: We amended the linkages to be made from silicone molds. For the code, fixed up the theta orientation function with Jack and printed new cages in a dark contrasting color to get the grayscale helper function to work as intended. Also used reference image function in Matlab for one of the cages Hexbugs to aid in tracking.

# Iteration IV - Three Bugs Plotting

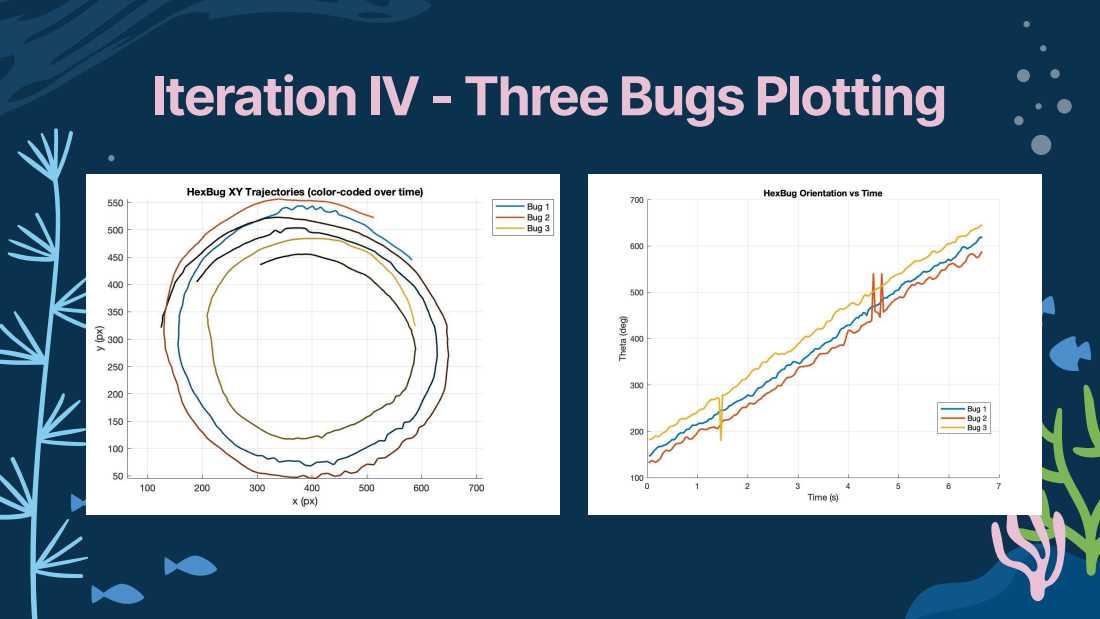
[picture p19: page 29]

# Iteration V

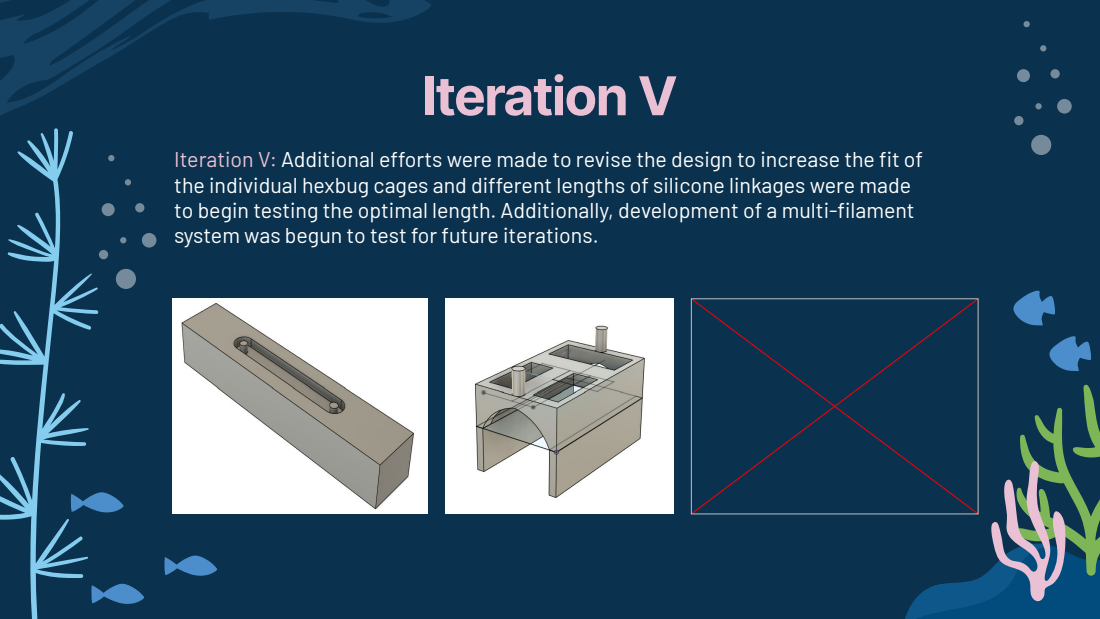
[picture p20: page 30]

Iteration V: Additional efforts were made to revise the design to increase the fit of
the individual hexbug cages and different lengths of silicone linkages were made
to begin testing the optimal length. Additionally, development of a multi-filament
system was begun to test for future iterations.

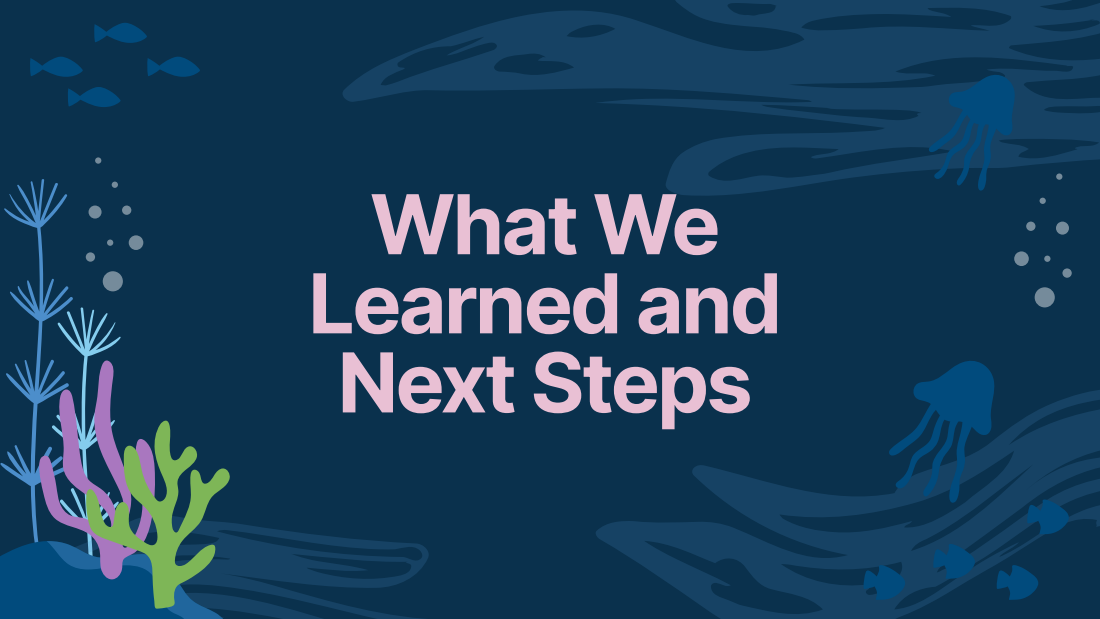
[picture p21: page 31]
What We Learned and Next Steps

# Preliminary Findings Summary

★ Evolved the physical setup of the experiment through iteration of the cages and linkages
- Developed molds for silicone which can be easily modified for whatever σ value we desire for a certain trial
■ Where σ determines whether the chain acts as a rigid line (high σ) or an elastic filament (small σ)
★ Easily adjustable cages and linkages allowed us to explore what types of experimental setups are feasible to achieve particular data collections
★ Having the connection point of the Hexbugs above the surface on which they move helps to reduce friction and show increased movement
★ Data tracking is sensitive but achievable by employing Matlab helper functions and color contrast between bugs and background
- Keeping code modular allows us to change number of particles as we see fit

# New Guiding Questions

★ What is the best way to consistently track our Hexbug’s orientation and position without experiencing spikes or dips?
- Is this a design change or a code change in order?
★ What will happen if we try to account for noise inherent to the bugs and the experimental setup?
- What does creating our own solver function in Matlab look like?
★ While changing the silicone molds is easy, the curing time is long; is there a way for us to use our numerical modeling more efficiently in order to cut down on the wait time between multiple linkage iterations?
★ Can we make our cages even more elevated off of the Hexbugs to make sure there is no skewing or interference with the legs?

# Roadblocks and Challenges

★ Design for homemade Hexbugs and utilizing a DV source for power
- Honing the 3D printable design for our accessible version of Hexbugs so that they do not just die once the battery dies (as seen with the store bought ones)
- Goal of trying to achieve Brownian-style motion in our bugs even though they are made of different materials than our current ones
- Getting circuitry to work, especially by troubleshooting the switches
★ Matlab struggling to totally orient the bug as it makes minor movements
- Could pose problems when we have smaller theta values due to code sensitivities

# Moving Forward and Next Steps

Design:
★ | Continuing to explore the balancing relationship between collective activity
| amongst particles and flexibility in the linkages
| ○ Honing design choices (i.e. thickness, length, cages, attachments,
| etc) to discover different phenomena
★ | Debugging circuitry for the homemade Hexbug
| ○ Playing around with dimensions in order to mimic similar movement
| to what we had seen
| ○ Getting switches and pager motors in line and functioning with the
| coin batteries
★ | Potentially exploring anti-friction design choices (i.e. ball bearings,
| air-hockey table)
Tracking:
★ | As we iterate into our own Hexbug design, we need to ensure that tracking
| capabilities are still functioning even though the “particles” are different
★ | Continue to hone smoothness in XY and theta plots

# Timeline

★ | 11/7: Assemble phase II model with 3D printed Hexbugs connected to direct voltage
| source via wiring. Conduct experimental trials of different numbers of Hexbugs in single
| filament
★ | 11/14: Continue phase II experimental trials, and analyze experimental data
★ | 11/21: Begin phase III model with multiple filaments attached to one fixed central body,
| mimicking a jellyfish.
★ | 11/28: Conduct phase III experimental trials, investigating the Hexbug orientations that
| move the fastest considering different lengths and numbers of filaments attached to the
| beam. Work on technical report
★ | 12/5: Complete open source Github, including CAD designs, code, raw and processed
| data as well as technical report
★ | 12/12: Finalize final presentation slides, practice presentations
★ | 12/13: Final presentation of deliverable, and final group evaluations

# Strategy

R6 - Remanufacture

We have manufactured our 3D printed cage to allow for multiple types of linkages between the hexbugs. Because we would want to analyze the effects of different lengths and types of linkages, the pegs on the cage allow for flexibility in the types of linkages we will able to test. This allows for longevity in the project. Also the cages are able to be easily attached and removed if a hexbug dies. If we decide to re-engineer our cage, we will continue to think of ways that will allow us to find multiple purposes of our material, to reduce as much waste as possible.

R3 - Reuse

Currently, in our preliminary stages, we have decided to use silicone to link our hexbugs together. We came upon this idea when talking to Jack about possible materials to link them together and he said that he had leftover silicone from an old project. Through collaboration, we found out that Andrew also had some leftover silicone from a different project, allowing us to use this material in our current iteration. Throughout the project we will continue to collaborate, as we were able to put old material to use that we would have not thought of otherwise.

# Proposed Budget

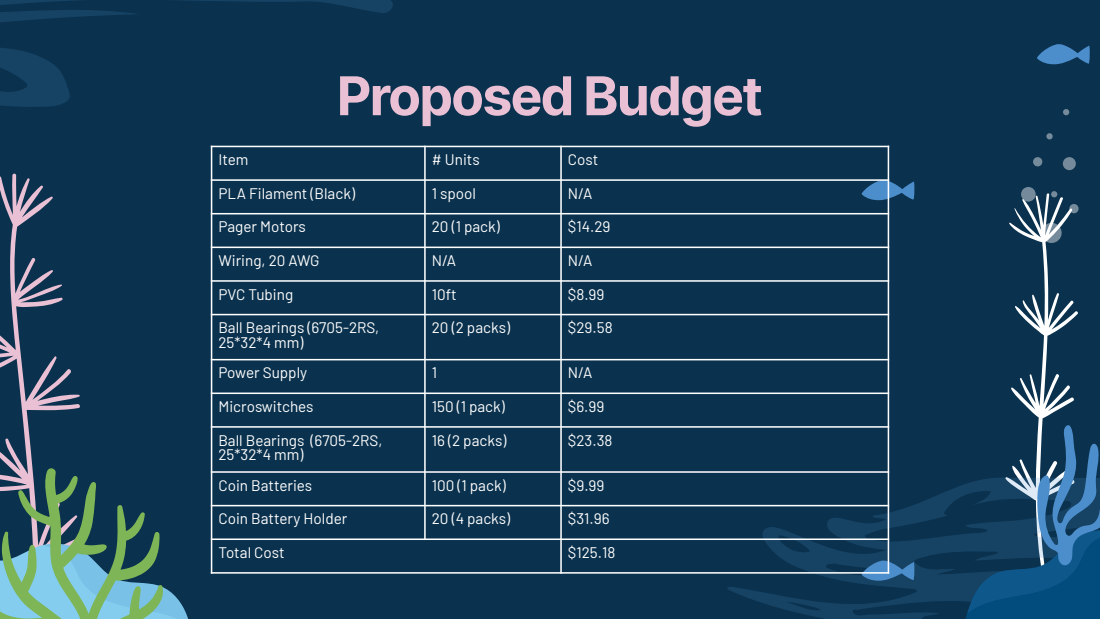
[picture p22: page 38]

Item | # Units | Cost
PLA Filament (Black) | 1 spool | N/A
Pager Motors | 20 (1 pack) | $14.29
Wiring, 20 AWG | N/A | N/A
PVC Tubing | 10ft | $8.99
Ball Bearings (6705-2RS, 25*32*4 mm) | 20 (2 packs) | $29.58

Power Supply | 1 | N/A
Microswitches | 150 (1 pack) | $6.99
Ball Bearings (6705-2RS, 25*32*4 mm) | 16 (2 packs) | $23.38

Coin Batteries | 100 (1 pack) | $9.99
Coin Battery Holder | 20 (4 packs) | $31.96
Total Cost | | $125.18

# Sources

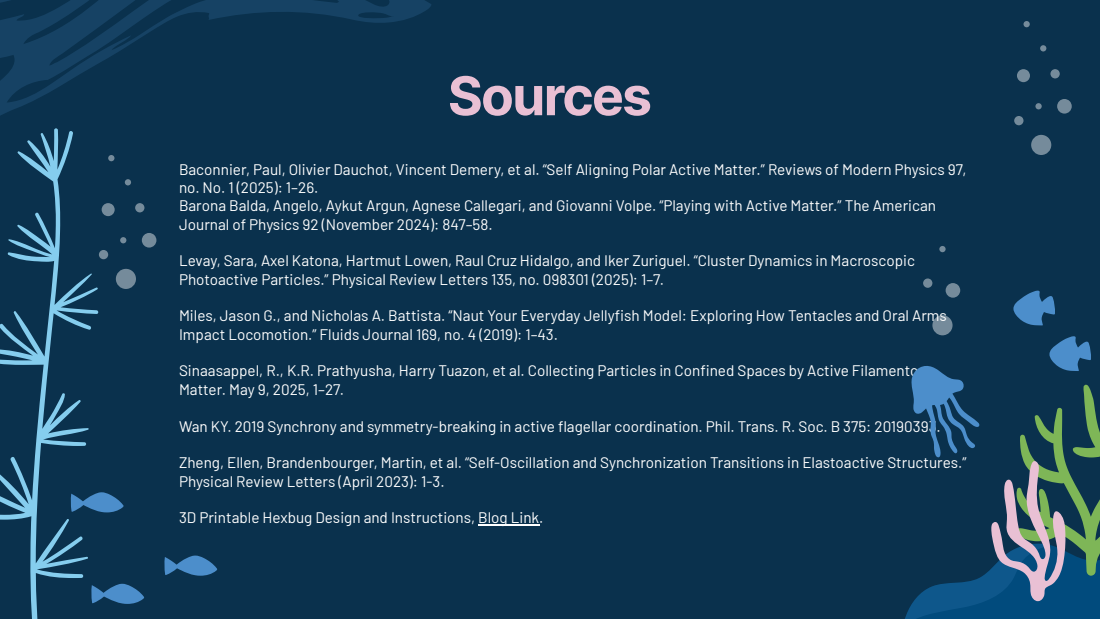
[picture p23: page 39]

Baconnier, Paul, Olivier Dauchot, Vincent Demery, et al. “Self Aligning Polar Active Matter.” Reviews of Modern Physics 97,
Barona Balda, Angelo, Aykut Argun, Agnese Callegari, and Giovanni Volpe. “Playing with Active Matter.” The American
Journal of Physics 92 (November 2024): 847–58.

Levay, Sara, Axel Katona, Hartmut Lowen, Raul Cruz Hidalgo, and Iker Zuriguel. “Cluster Dynamics in Macroscopic
Photoactive Particles.” Physical Review Letters 135, no. 098301 (2025): 1–7.

Miles, Jason G., and Nicholas A. Battista. “Naut Your Everyday Jellyfish Model: Exploring How Tentacles and Oral Arms
Impact Locomotion.” Fluids Journal 169, no. 4 (2019): 1–43.

Sinaasappel, R., K.R. Prathyusha, Harry Tuazon, et al. Collecting Particles in Confined Spaces by Active Filamentous
Matter. May 9, 2025, 1–27.

Wan KY. 2019 Synchrony and symmetry-breaking in active flagellar coordination. Phil. Trans. R. Soc. B 375: 20190393.

Zheng, Ellen, Brandenbourger, Martin, et al. “Self-Oscillation and Synchronization Transitions in Elastoactive Structures.”
Physical Review Letters (April 2023): 1-3.

3D Printable Hexbug Design and Instructions, Blog Link. (https://stldenise3d.com/vibrobugs-3d-printed-brush-bots/)

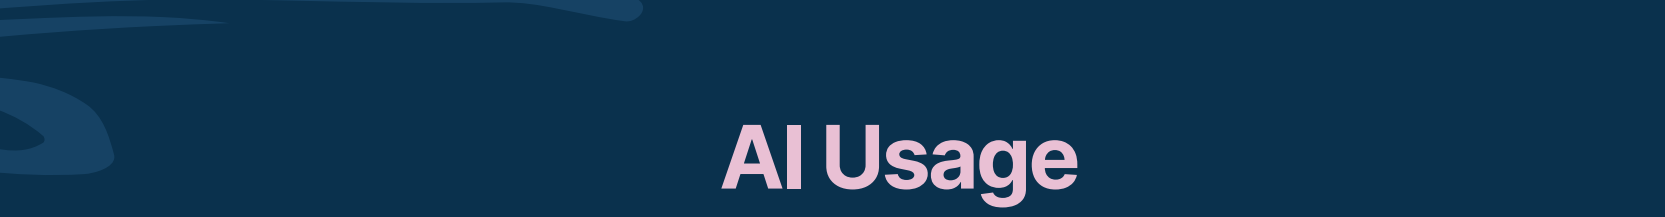
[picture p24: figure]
AI Usage

Tracker Code and Embedded Image Processing - Our tracking code bridges two source codes: one from Fluid Dynamics ENGN 810 for scale image processing and the other from our project partner, Jack-William Barotta’s, research on the rotation and tracking of spinners. ChatGPT was used to bridge these codes and supplement debugging.
- Prompts used:
- Conceptually explain how this tracking code for spinners can be translated to particle tracking
■ Provided us with overall guidance as to what we were able to keep in our tracking code and what we could get ride of in the context of our problem
- Provide helper functions for image contrasting and box tracking
■ Aided in making our video into grayscale to exacerbate differences between the bugs and the platform we were running our trials on. And then adjusted the bounding boxed around the bugs after initialization clicks occurred to better track the bugs as they travel.

Tracker Code and Embedded Image Processing
- Prompts used (cont.)
- Provide debugging help for mregform function
■ We were running into issues employing what was originally from Jack’s code for spinners into our scenario for the hexbugs. Making great contrast in colors helped, but AI was able to add parts of the script to tighten orientation tracking through this function
- Make plots prettier, please
■ Provided small code for using latex for aces, larger legends, gridlines, and other visually appealing aspects to make our plotting more clear to viewers

Spring Constant Image Processing and Young’s Modulus Calculation - When calculating the Spring constant, we examined the deflection of the beam as we added weights across beams of all three lengths. Through this process, we collected a numerous amount of photos, where we decided image processing using Matlab to collect the data and find the spring constant for us. We then took that spring constant data and used Matlab to quickly compute the Young’s Modulus
- Prompts used:
- Create a Matlab script to calculate the spring constant of beams. We have 3 folders, named small, medium, and large, all filled with jpegs that are named the mass in grams. In each of the photos prompt the user to click the beginning and end of the beam, and then in that same photo prompt the user to click 100mm on a ruler to scale for mm/pixel
- Create a Matlab script to calculate the Young’s Modulus given the last code. The cross sectional area is a rectangle.

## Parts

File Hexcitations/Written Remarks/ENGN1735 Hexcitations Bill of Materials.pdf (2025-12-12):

ENGN1735: Hexcitations
Bill of Materials

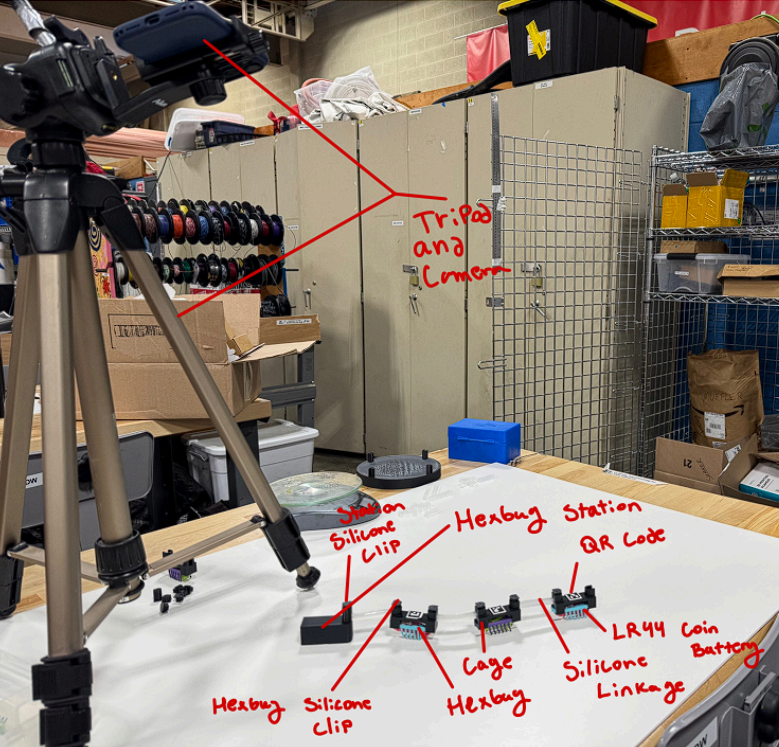
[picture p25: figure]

Component | Quantity | Material
Hexbug | 3 | Various electronic, plastic, rubber, and metal materials
Hexbug Cage | 3 | PLA Filament
Hexbug Station | 1 | PLA Filament
Silicone Linkage | 3 | Silicone
Hexbug Station Silicone Linkage Clip | 5 | PLA Filament
Hexbug Cage Silicone Linkage Clip | 1 | PLA Filament
QR Codes | 3 | Paper
Tripod | 1 | Metal & Plastic
Backing Paper | 1 | Paper
LR44 Coin Batteries | 3 | Various electronic materials

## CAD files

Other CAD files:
Hexcitations/CAD Designs/Cage Design/Iteration I/hexbug casing v6.f3d
Hexcitations/CAD Designs/Cage Design/Iteration I/hexbug casing_revised size v2.f3d
Hexcitations/CAD Designs/Cage Design/Iteration II/hexbug case v1.f3d
Hexcitations/CAD Designs/Cage Design/Iteration III/hexbug case v2.f3d
Hexcitations/CAD Designs/Cage Design/Iteration IV (final)/hexbug_cage_final.f3d
Hexcitations/CAD Designs/Linkage Design/Iteration I/hexbug_3.5cm_mold v1.f3d
Hexcitations/CAD Designs/Linkage Design/Iteration I/hexbug_4.5cm_mold v1.f3d
Hexcitations/CAD Designs/Linkage Design/Iteration I/hexbug_5.5cm_mold v1.f3d
Hexcitations/CAD Designs/Linkage Design/Iteration II (final)/hexbug_2.5cm_mold_final.f3d
Hexcitations/CAD Designs/Linkage Design/Iteration II (final)/hexbug_3.5cm_mold_final.f3d
Hexcitations/CAD Designs/Linkage Design/Iteration II (final)/hexbug_4.5cm_mold_final.f3d
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

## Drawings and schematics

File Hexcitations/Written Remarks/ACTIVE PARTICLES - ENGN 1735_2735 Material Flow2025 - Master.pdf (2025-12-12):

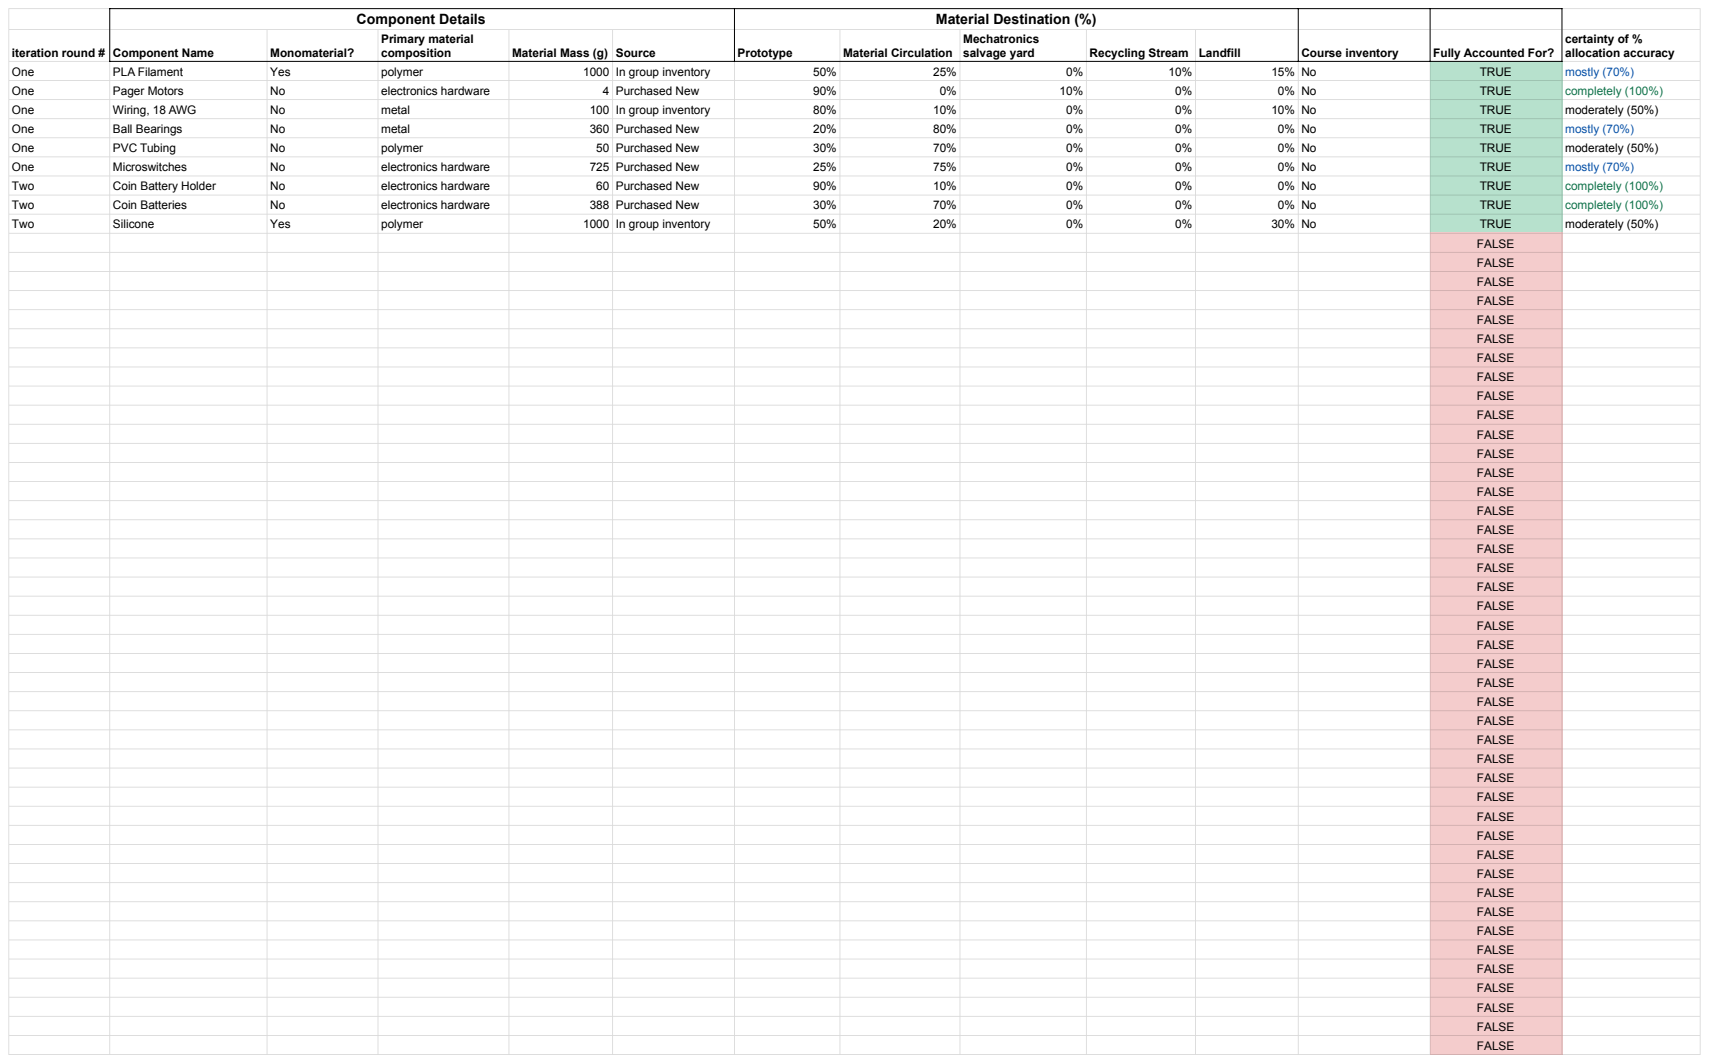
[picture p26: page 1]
Component Details; Material Destination (%); iteration round #; Component Name; Monomaterial?; Primary material; composition; Material Mass (g) Source; Prototype; Material Circulation; Mechatronics; salvage yard; Recycling Stream Landfill; Course inventory; Fully Accounted For?; certainty of % allocation accuracy; One; PLA Filament; Yes; polymer; 1000 In group inventory; TRUE; mostly (70%); Pager Motors; electronics hardware; 4 Purchased New; completely (100%); Wiring, 18 AWG; metal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
